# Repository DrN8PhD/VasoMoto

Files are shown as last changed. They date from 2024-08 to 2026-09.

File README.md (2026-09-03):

# VasoMoto
## Monitor and control cannulated vessel pressure in one easy-to-build unit

This arduino-based code is used to program the VasoMoto controller.
Paired with [VasoTracker-2 software](https://github.com/VasoTracker/VasoTracker-2), intravascular pressure can be monitored and controlled without the need for costly interface units.

This system is also capable of simulating pulsatile changes in pressure at rates approaching normal murine heart rate (~400 bpm). A few notes:

* While adaptable to other Arduino versions, this code is specifically written to utilize SAMD51-based microcontrollers. The [ItsyBitsy by Adafruit Inc.](https://www.adafruit.com/product/3800) is recommended.
* A myriad of libraries are required in addition to the custom ones included here.
* The parts list and assembly manual are also included in the release packages.
* This system requires a custom PCB. This is available at a nominal cost through the [Cubi<sup>3</sup>C Core Facility](https://phmtox.msu.edu/facilities/cubi3c) at Michigan State University. Costs will vary depending on the level of assembly you want, but I assure you -- it's far less than any other system on the market.

## v5.0.1
* Bug fixes I missed. 
## v5.0
* This is a complete overhaul of the system's code. Changes for increased stability, better responsiveness and accuracy. Also maintains backward compatibility with original systems.
* Pressure ramps and pulse simulation are functional.
* Pulse simulation gets unpredictable over ~200 bpm. But I call that a win for now.
* Added line filling feature to speed setup of an experiment. It also has a pressure control so you can't destroy your vessel.
* All the menus are now accessible without having to reset the entire box. Calibrations, modes, advanced settings...all can be reached without severing the serial connection to the computer.

## v4.2
* First major update. I noticed that the sampling rate was too high relative to the pressure sensing resolution, resulting in weird pressure oscillations that I couldn't notice until we were tracking pressure with VasoTracker 2. This should all be fixed, resulting in better, more accurate pressure regulation. It's a bit slower for the line filling at first, but this is a small price to pay for healthier vessels.

## v4.1.1
* Added slow pressure ramp. This is different than the step protocol in VasoTracker. This slowly increases the set pressure at a given rate in mmHg/minute.
  
## v4.1.0
* Multiple bug fixes.
* Additional code to allow VasoTracker to control pressure and do timed pressure steps without the need for NI interface.
* Additoonal commenting throughout for clarity in the Arduino code.

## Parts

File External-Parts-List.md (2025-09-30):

# External Parts list
## Here is what you need to purchase to complete this build (USA):

* 3D printed parts included in this GitHub.
* Adafruit [ItsyBitsy M4 Express](https://www.adafruit.com/product/3800). Be sure to get the male and female headers as well! You'll need both to build yourself.
* Stepper motor driver, with equivalent pinout to [this one using the TMC2209 driver](https://www.amazon.com/gp/product/B07ZPV4HFP/).
* [1.8" LCD display module](https://www.amazon.com/gp/product/B07VBSZ2HX).
* [Rotary encoder](https://www.amazon.com/gp/product/B06XQTHDRR/). You will need to modify slightly to change orientation of the pins. So a little soldering is unavoidable until I find an encoder without pins that isn't junk. Note: __this is not a potentiometer__.
* 1.8° stepper motor. Either [NEMA-17](https://www.amazon.com/STEPPERONLINE-Bipolar-Stepper-22-6oz-Extruder/dp/B00PNEQ79Q/) or [NEMA-11](https://www.amazon.com/Iverntech-Stepper-Printer-Machine-Robotics/dp/B07PNV7RBW/) will work with the unit as designed.
* Adjustable AC/DC power supply. I usually use [this one](https://www.amazon.com/gp/product/B07N18XN84/) since it has other tips to use long0-term. __This setup runs at 7.5V__.
* [Silicone tubing](https://www.amazon.com/VictorsHome-Silicone-Flexible-Transfer-Transparent/dp/B09DKWWRSG) with 0.5 mm wall thickness. O.D. does not matter; pump works with 2 mm O.D. – 4 mm O.D. tubing.
* 4-wire pressure transducer. I prefer [these disposable ones from MedLine](https://www.medline.com/product/Head/Z05-PF154670). You can either replace the RJ-11 connector or just cut the robber off to make it more accessible.
* Luer connectors. But if you're reading this, it's my guess you have a box of them in your lab somewhere anyway. (c:
* 3/16" (or 5 mm) set screws. The design used 4-40 thread size since I'm in the USA, but any roughly equivalent diameter will work. 3 are needed for the pump wheel.
* Miscellaneous M3 button cap hex machine screws. Nothing fancy, but the length will depend on which motor you choose.
* [Dry-running MDS-filled nylon sleeve bearing](https://www.mcmaster.com/6294K401/). This is the exact one I used, and you need 3 of them.
* [Acetal dowel pins](https://www.mcmaster.com/97155A426/). These are also the exact ones I use (1/8" diameter, 1/2" long; sorry to metric system colleague). You will need 3 total, but they come in a pack of 50.

### Lastly:
* *PCB with 2-channel custom instrumentation amplifier, integrated stepper motor control and 16-bit ADC ($495 through the MSU Cubi3c Core Facility).*

## Note on the PCB:
So there are probably other ways to do this off-the-shelf, but I designed and built a board for this. I am working on how to make it available through my facilities here at MSU, so please be patient. If you're good at soldering and have a forced-air soldering device, this is doable as a DIY. Otherwise it takes me about 90 minutes to put one together. Futher details on this are available by request.

## Here is what you need to purchase to complete this build (UK):

* 3D printed parts included in this GitHub.
* [Adafruit ItsyBitsy M4 Express (w/ headers)](https://www.digikey.co.uk/en/products/detail/adafruit-industries-llc/3800/9448047).
* [BigTreeTeach TMC2209 V1.3 Stepper motor driver ](https://www.3djake.uk/bigtreetech/stepper-motor-driver?sai=9875).
* [1.8" LCD display module](https://www.amazon.com/gp/product/B07VBSZ2HX).
* [Rotary encoder](https://www.amazon.co.uk/KY-040-Encoder-Development-Arduino-including/dp/B09726Y8RB). 
* 1.8° stepper motor. Either [NEMA-17](https://www.omc-stepperonline.com/nema-17-bipolar-1-8deg-16ncm-22-6oz-in-1a-3-7v-42x42x20mm-4-wires-17hs08-1004s) or [NEMA-11](https://www.amazon.com/Iverntech-Stepper-Printer-Machine-Robotics/dp/B07PNV7RBW/) will work with the unit as designed.
* [Adjustable AC/DC power supply](https://www.amazon.co.uk/Outtag-Universal-Adapter-Speakers-Routers-Black/dp/B0CKYMPDBY/) 
* [Silicone tubing](https://www.amazon.co.uk/VictorsHome-Silicone-Length-Flexible-Transparent/dp/B0CBJWK7XC/) with 0.5 mm wall thickness. O.D. does not matter; pump works with 2 mm O.D. – 4 mm O.D. tubing.
* 4-wire pressure transducer. I prefer [these disposable ones from MedLine](https://www.acevetsupplies.co.uk/products/ibp-transducer-kit-medex-abbott-42585-05). You can either replace the RJ-11 connector or just cut the robber off to make it more accessible.
* Luer connectors. But if you're reading this, it's my guess you have a box of them in your lab somewhere anyway. (c:
* [3x 3/16" (or 5 mm) set screws. 4-40 thread](https://www.accu.co.uk/imperial-cup-point-setgrub-screws/31301-SSU-4-40-3-16-A4)
* [Miscellaneous M3 button cap hex machine screws](https://www.amazon.co.uk/Stainless-Precise-Tapping-Washers-Assortment/dp/B09J2MNSMZ)
* [3x Needle roller bearings](https://www.bearingboys.co.uk/HK-Series-Drawn-Cup-Needle-Bearings/HK0306-Budget-Drawn-Cup-Needle-Bearing-356063-p) (instead of nylon sleeve bearings)
* [Needle Roller Pins](https://www.bearingboys.co.uk/Loose-Needle-Rollers/3mm-x-118mm-Round-End-Loose-Needle-Rollers-Pack-of-100-456051-p) (instead of acetal dowel pins)

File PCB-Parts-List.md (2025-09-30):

# PCB Parts List
### For those looking for a fun way to spend an afternoon!

|  Qty  |  Description  |  Price  |  Total  |
|  ---  |  ---  |  ---  |  ---  |
|  1  |  Custom VasoMoto4 PCB (v1)  |  $40.00  |  $40.00  |
|  1  |  [Adafruit ItsyBitsy M4](https://www.adafruit.com/product/3800)  |  $14.95  |  $14.95  |
|  1  |  [1.8" SPI TFT Display](https://www.amazon.com/1-8inch-LCD-Display-Module-Communicating/dp/B07VBSZ2HX?th=1)  |  $13.43  |  $13.43  |
|  1  |  [NEMA 17 Stepper Motor (short body)](https://www.amazon.com/STEPPERONLINE-Bipolar-Stepper-22-6oz-Extruder/dp/B00PNEQ79Q)  |  $11.99  |  $11.99  |
|  1  |  [TMC2209 Stepper Driver](https://www.amazon.com/BIGTREETECH-TMC2209-Stepper-Printer-Motherboard/dp/B08SMDY3SQ/?th=1)  |  $13.99  |  $13.99  |
|  1  |  [Rotary Encoder](https://www.amazon.com/gp/product/B06XQTHDRR)  |  $9.29  |  $9.29
|  1  |  [DC Power Jack with Switch](https://www.adafruit.com/product/3642)  | $1.95	|	$1.95 |
|  1  |  [AD8426ACPZ Amplifier](https://www.mouser.com/ProductDetail/Analog-Devices/AD8426ACPZ-R7?qs=%2FtpEQrCGXCy0%2F9Zrxy%252BnYw%3D%3D)  | $8.24	|	$8.24 |
|  2  |  [ADA4500 Amplifier](https://www.mouser.com/ProductDetail/Analog-Devices/ADA4500-2ARMZ?qs=BpaRKvA4VqHOSyw3sQK59Q%3D%3D)  | $4.97	|	$9.94 |
|  1  |  [ADS1115 16-bit ADC](https://www.mouser.com/ProductDetail/Texas-Instruments/ADS1115BQDGSRQ1?qs=34RfhUjJmKdvyLrkbnfjHA%)  | $5.83	|	$5.83 |
|  1  |  [L7805CV Linear Voltage Regulator (5 V)](https://www.mouser.com/ProductDetail/STMicroelectronics/L7805CV?qs=9NrABl3fj%2FqplZAHiYUxWg%3D%3D)  | $0.50	|	$0.50 |
|  2  |  [RJ25 Jack](https://www.mouser.com/ProductDetail/571-5555165-1)  | $0.99	|	$1.98 |
|  1  |  [ItsyBitsy Female Headers (Pack)](https://www.adafruit.com/product/4174)  | $1.25	|	$1.25 |
|  2  |  [8-pin Female Header](https://www.mouser.com/ProductDetail/TE-Connectivity/535541-6?qs=ZDXmSm13592BeyHKSexOiA%3D%3D)  | $1.41	|	$2.82 |
|  1  |  [Male Pin Headers (minimum 20 total pins)](https://www.mouser.com/ProductDetail/Molex/22-28-4200?qs=GAPJcf4kvdv8LEkug6BEWQ%3D%3D)  | $0.86	|	$0.86 |
|  6  |  [1x2 Screw Terminal (3.5 mm)](https://www.mouser.com/ProductDetail/Adam-Tech/EBWA-02-A?qs=HoCaDK9Nz5cgBIK%2FOdkl1w%3D%3D)  | $0.49	|	$2.94 |
|  2  |  [10 kOhm Trimmer Resistor](https://www.mouser.com/ProductDetail/652-3314J-1-103E)  | $1.58	|	$3.16 |
|  1  |  [100 µF aluminum polymer capacitor](https://www.mouser.com/ProductDetail/Panasonic/16SEPC100M%2bTSS?qs=OE1iw1LrrPEAt2lEmEitdA%3D%3D)  | $0.89	|	$0.89 |
|  1  |  [10 µF capacitor (US1206)](https://www.mouser.com/ProductDetail/YAGEO/CC1206ZKY5V7BB106?qs=rEZiXmXGZa%2FuXF99zRq3Vg%3D%3D)  | $0.24	|	$0.24 |
|  1  |  [0.33 µF ceramic capacitor](https://www.mouser.com/ProductDetail/KEMET/C324C334M5U5TA?qs=sGAEpiMZZMsh%252B1woXyUXj%2FPRwpp8kXWD%2F6VAC8Qms%2F0%3D)  | $0.49	|	$0.49 |
|  1  |  [0.1 µF capacitor (US1206)](https://www.mouser.com/ProductDetail/KEMET/C1206C104K5RACTU?qs=VbFpUC1cecnmBMAUeCQCPw%3D%3D)  | $0.10	|	$0.10 |
|  2  |  [0.015 µF (15 nF) capacitor (US1206)](https://www.mouser.com/ProductDetail/KEMET/C1206C153K5RACTU?qs=kei6kuvHAl88e3ElWIo0oA%3D%3D)  | $0.21	|	$0.42 |
|  7  |  [0.01 µF (10 nF) capacitor (US1206)](https://www.mouser.com/ProductDetail/KEMET/C1206C103M5RACTU?qs=C9xViIFka8k6tXd6%2Fqf7IA%3D%3D)  | $0.11	|	$0.77 |
|  2  |  [14.3 kOhm Resistor (US1206)](https://www.mouser.com/ProductDetail/YAGEO/RC1206FR-0714K3L?qs=ncxkyCpAYDBq1S9aCtJYCQ%3D%3D)  | $0.10	|	$0.20 |
|  3  |  [10 kOhm Resistor (US1206)](https://www.mouser.com/ProductDetail/YAGEO/RC1206FR-0710KL?qs=%252BhB4WxZmbVEJV82xdVgRUw%3D%3D)  | $0.10	|	$0.30 |
|  2  |  [7.32 kOhm Resistor (US1206)](https://www.mouser.com/ProductDetail/YAGEO/RC1206FR-077K32L?qs=afJZr%2F7kGG6v1eT3E1VQ7A%3D%3D)  | $0.10	|	$0.20 |
|  2  |  [91 Ohm Resistor (US1206)](https://www.mouser.com/ProductDetail/YAGEO/RC1206JR-0791RL?qs=2fXw4cjoqb%2FCE9bK5gFcaQ%3D%3D)  | $0.10	|	$0.20 |
|  1  |  [3V – 12VDC power supply](https://www.amazon.com/gp/product/B07N18XN84)  | $15.90	|	$15.90 |
|  1  |  [Crimping Tool Kit](https://www.amazon.com/gp/product/B07R1H3Z8X)  | $34.99	|	$34.99 |
|  ---  |  ---  |  ---  |  ---  |
|    |    |  **Total:**  |  **$197.82**  |

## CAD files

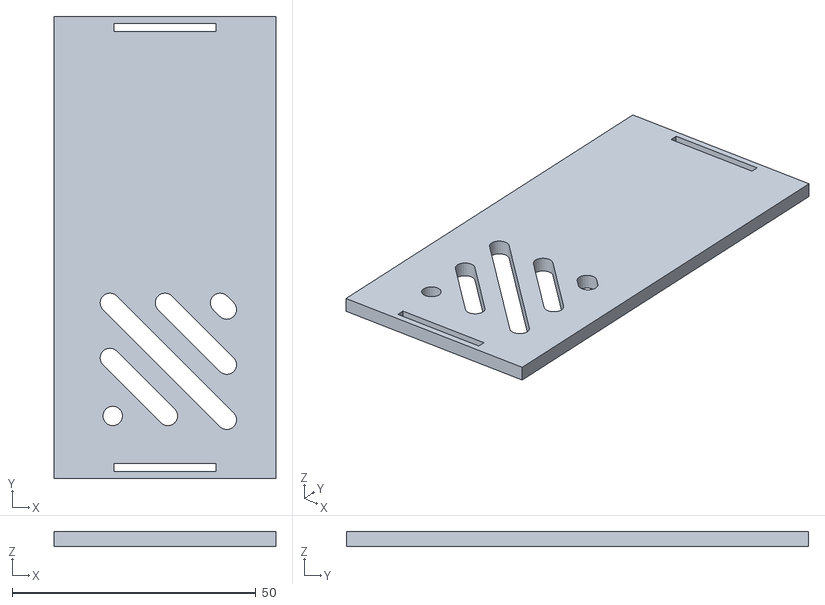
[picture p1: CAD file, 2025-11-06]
VasoMoto Printed Parts/VasoMoto-front.stl
45.5 x 94.8 x 3.00

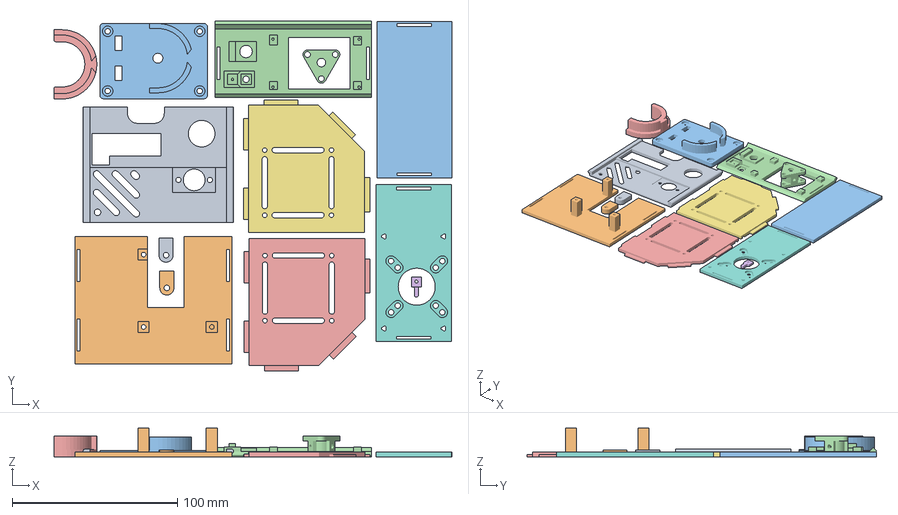
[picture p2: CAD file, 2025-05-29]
VasoMoto Printed Parts/VasoMoto_Core_One_All.3mf
240.8 x 211.5 x 17.5 mm
VasoMoto-back.stl
VasoMoto-base.stl
VasoMoto-front.stl
VasoMoto-LCD-button.stl
VasoMoto-left-side.stl
VasoMoto-optional-clip.stl
VasoMoto-right-side.stl
VasoMoto-Top.stl
VasoMoto-tube-holder.stl x 2
VasoMoto-pump.stl
VasoMoto-pumphead.stl
VasoMoto-tubing-spacer-2.stl

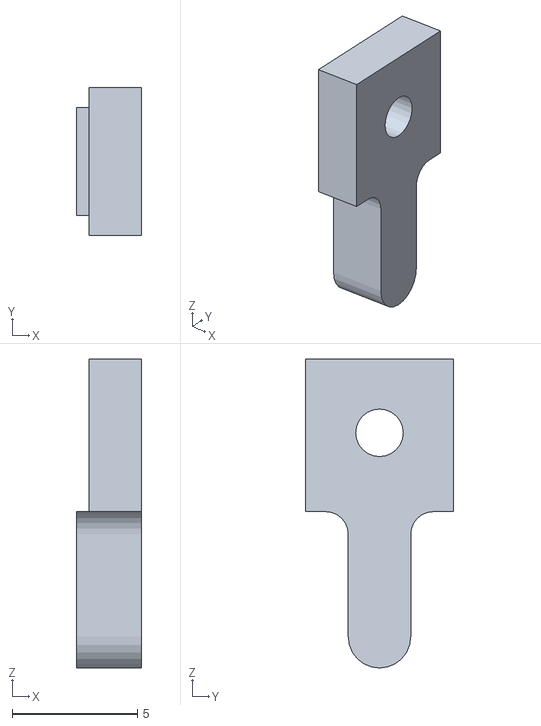
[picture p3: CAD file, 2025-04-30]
VasoMoto Printed Parts/VasoMoto-optional-clip.stl
2.60 x 5.90 x 12.3

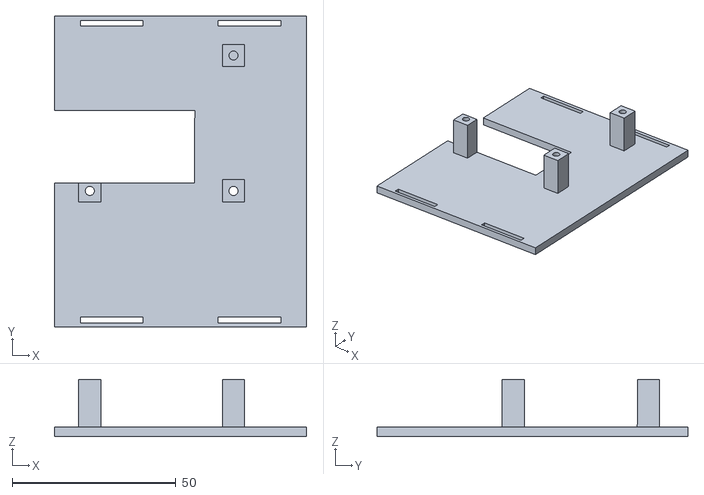
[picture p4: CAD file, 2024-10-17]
VasoMoto Printed Parts/VasoMoto-base.stl
76.9 x 94.8 x 17.5

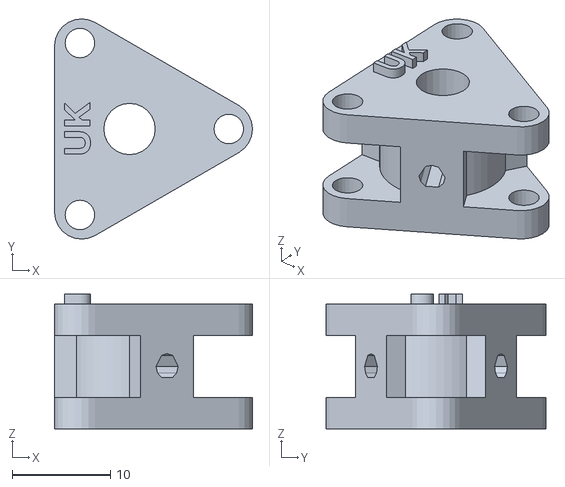
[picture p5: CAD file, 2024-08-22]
VasoMoto Printed Parts/VasoMoto-pumphead-UK.stl
20.1 x 22.4 x 13.7

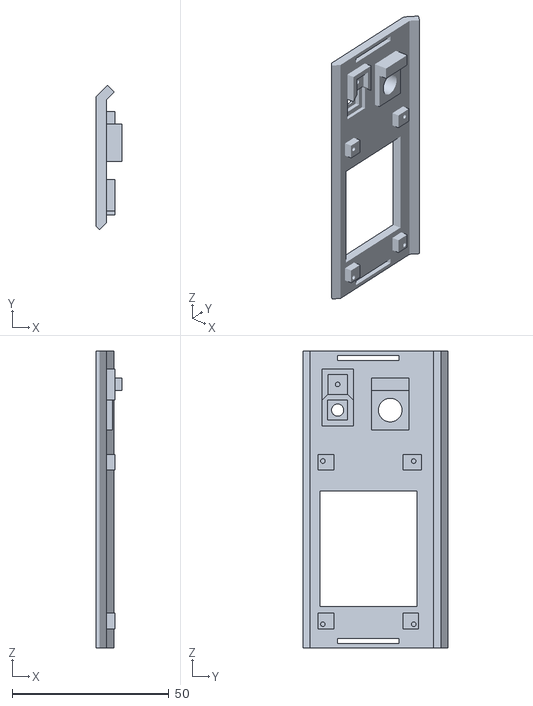
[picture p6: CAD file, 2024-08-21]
VasoMoto Printed Parts/VasoMoto-LCD-button.stl
8.29 x 46.2 x 94.8

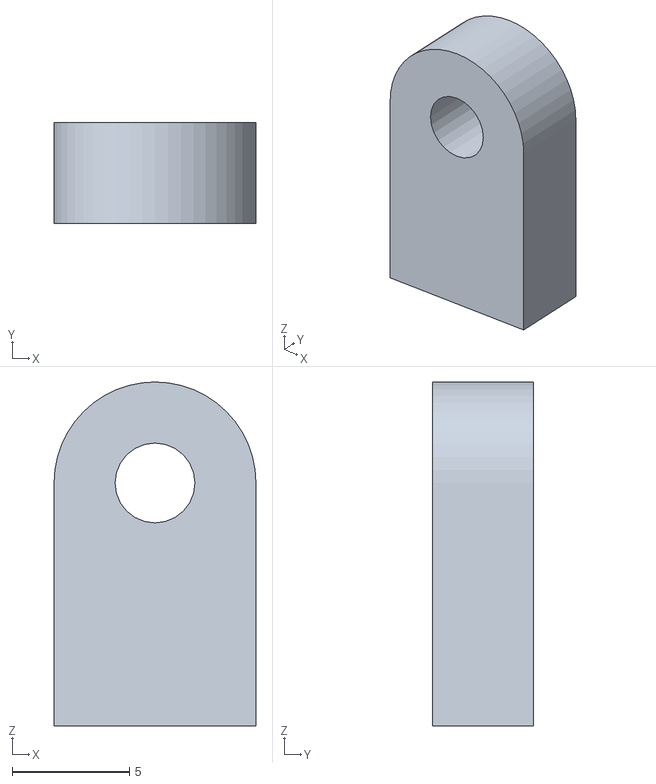
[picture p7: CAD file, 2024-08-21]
VasoMoto Printed Parts/VasoMoto-tube-holder.stl
8.60 x 4.30 x 14.7

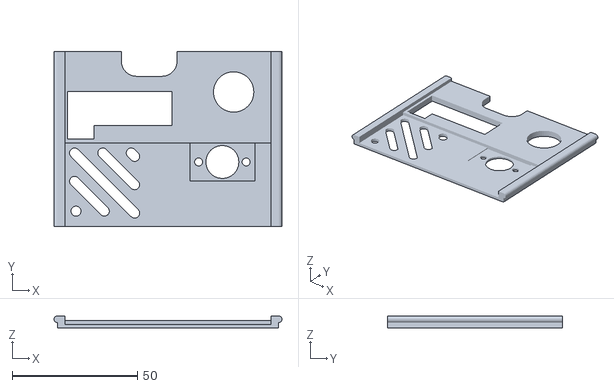
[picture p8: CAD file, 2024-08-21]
VasoMoto Printed Parts/VasoMoto-back.stl
91.0 x 70.0 x 4.80

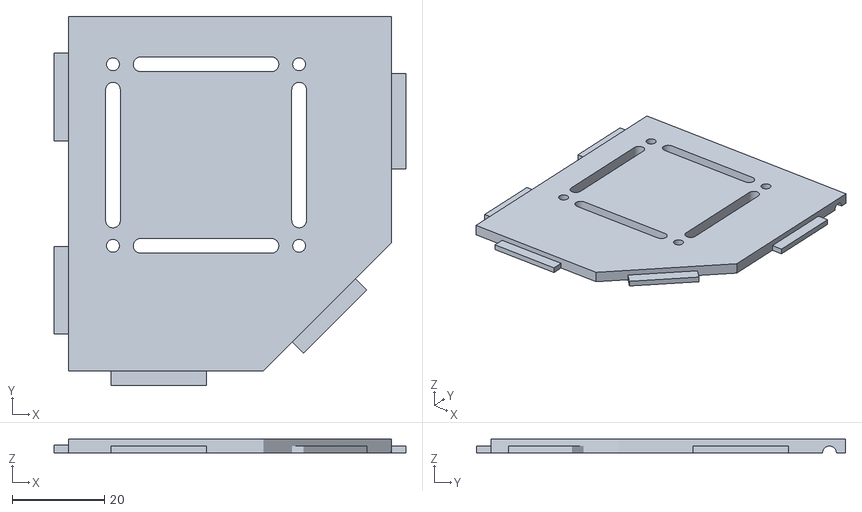
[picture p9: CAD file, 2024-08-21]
VasoMoto Printed Parts/VasoMoto-left-side.stl
76.4 x 80.1 x 3.03

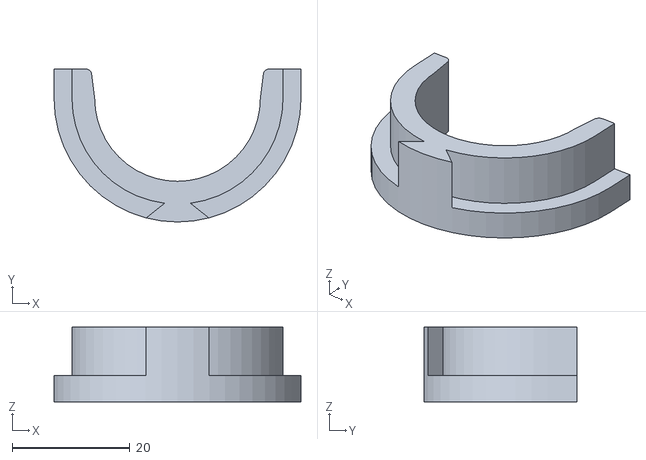
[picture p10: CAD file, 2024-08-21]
VasoMoto Printed Parts/VasoMoto-tubing-spacer-1.stl
41.9 x 26.0 x 12.7

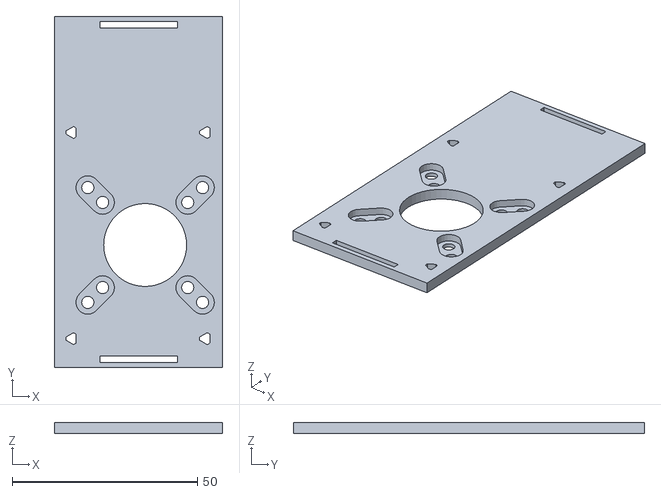
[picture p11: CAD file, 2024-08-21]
VasoMoto Printed Parts/VasoMoto-Top.stl
45.5 x 94.8 x 3.00

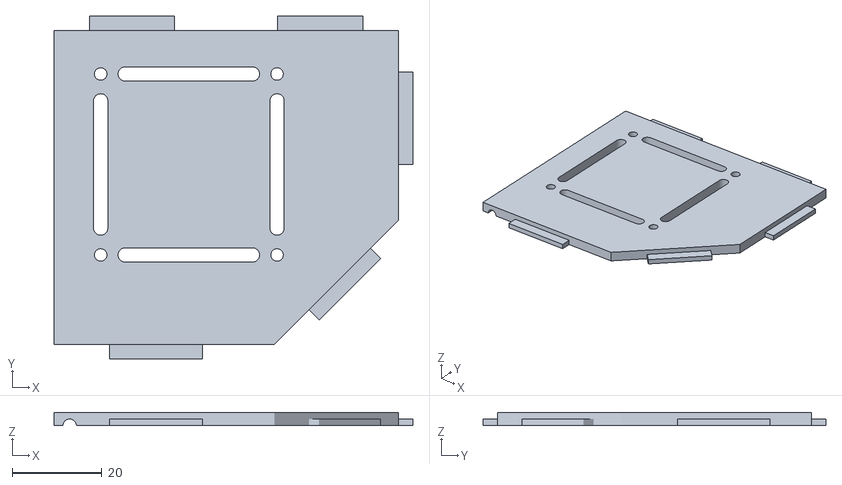
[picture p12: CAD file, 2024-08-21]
VasoMoto Printed Parts/VasoMoto-right-side.stl
80.1 x 76.5 x 3.00

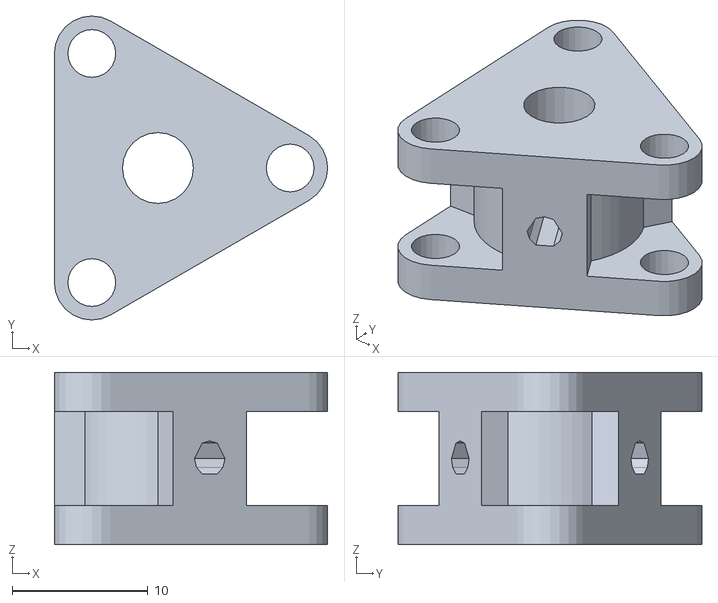
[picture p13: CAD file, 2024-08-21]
VasoMoto Printed Parts/VasoMoto-pumphead.stl
20.1 x 22.4 x 12.7

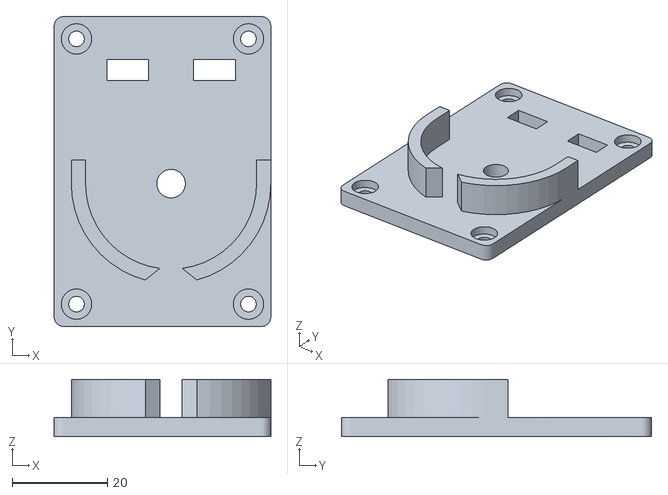
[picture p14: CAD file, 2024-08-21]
VasoMoto Printed Parts/VasoMoto-pump.stl
45.5 x 65.1 x 12.0

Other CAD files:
VasoMoto Printed Parts/VasoMoto-LCD-no-button.stl
VasoMoto Printed Parts/VasoMoto-tubing-spacer-2.stl

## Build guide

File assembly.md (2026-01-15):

# Assembly Instructions
## Prior to Beginning:
1) Acquire all parts listed in the "external-parts-list.md" file.
2) Print all required parts in the "VasoMoto Printed Parts" folder. Note that UK and US have different pump heads to print. This is due to differences in parts availability. The UK parts are prototyped, but not tested in practice yet.
3) Every rotary encoder I can find has bent pins that are on the wrong side. You will need to de-solder the 5 bent pins and solder 5 straight pins in their place. Make sure the ones you're replacing are on the **opposite side of the circuit board from the knob.** See below for a clearer picture.
4) This guide assumes you have fabricated or purchased the completed PCB that makes up the "heart" of the VasoMoto controller. A separate manual in the works for how to fabricate the VasoMoto controller from scratch with the "blank" PCB.

##  **Step 1: Lay out all the pieces.**
Everything is shown here, except the pump head and fasteners. They'll be pictured later. The pieces are as follows:
1)  Front plate
2)  Stepper motor NEMA 17 stepper motor
3)  Pump plate
4)  VasoMoto controller PCB
5)  LCD plate
6)  1.8" LCD module
7)  Back plate
8)  Arduino
9)  Rotary encoder and stepper motor driver
10) Motor plate
11) Left side plate
12) Right side plate
13) Base plate
VasoMoto parts laid out

##  **Step 2: Get the fasteners together.**
Fasteners needed are shown below. Where there is flexibility in sizing, I've made that note. We will be assembling efverything __but__ the pump head right now.

1)  1/4" No. 2 sheet metal screws (4). These need to be the 'pointy' kind of screw. They attach the LCD diplay to the LCD plate.
2)  M3 x 4 mm button cap screws (4). These are the 'flat' kind of screws. They attach the motor to the motor plate
3)  M3 x 6 mm button cap screws (4). THey can be longer than 6 mm but not shorter. They attach the pump to the motor plate.
4)  The screws off of the LCD display stand-offs (3). If you got an LCD without these screws, just use 3 more M3x6 screws instead.

assembly screws

##  **Step 3: Assemble VasoMoto controller.**
Insert the arduino in the bottom of the PCB in the appropriate headers. Insert the stepper motor driver in the proper headers on the top. Note that the proper "DIR" and "GND" pins on the header are in the spots marked "DIR" and "GND" on the PCB.

Assembled PCB

##  **Step 4: Attach the VasoMoto controller top the base plate.**
Use 3 screws. THe holes aren't threaded, so it might be easier to screw them in without the controller first to cut some threads in the plastic. You might have to pop the stepper driver back out, depending on what size screw and screwdriver you have.

PCB affixed to baseplate

##  **Step 5: Assemble the LCD plate.**
1) If opresent, remove all 4 brass standoffs from the display. no need to connect any cables just yet. Not the direction of the connector -- the LCD only fits in the plate one way. LCD in LCD plate
2) Using 4 No. 2 machine screws, attach the LCD module to the LCD plate. Do NOT overtighten, or the screws will poke through the front of the plate.
3) Insert the rotary econder with the pins placed as noted in the photo. Ignore that extra wire and button -- that's not needed for this build. Attach the rotary encoder using the nut and washer that comes with it.

LCD and rotary encoder in place

##  **Step 6: Prepare and connect the rotary encoder wiring harness.**
These next two parts Are probably the trickier bits since there are a bunch of different ways to do it. I have a crimper and connectors, so I make my own wires. But this can be done with [10 cm female-to-female jumper wires](https://www.amazon.com/dp/B07S2RH6Q4/).
 1)  Connect the roatry encoder to the VasoMoto controller using 5 jumper wires. This is the easy part. Each pin's identity is printed on the front, so the image below tells you what each one is. 

rotary encoder pinout
PCB pinout for encoder

2)  Once connected, it should look like the image below. As you can see I have 5-pin DIN headers and shorter wires, but there is plenty of space in the VasoMoto enclosure to cram the excess 10 cm retail jumper wires.

connected encoder

##  **Step 7: Prepare and connect the LCD wiring harness.
Now for the trickier part. If you can, get some [8-pin female dupont connector housings](https://www.amazon.com/2-54mm-Dupont-Connector-Housing-Female/dp/B0BG7CZ2F9/). This makes connecting and disconnecting a LOT easier....but you can also use the connectors on the LCD harness if you want to save a few bucks. The reaason the order is different on the board compared to the module is...complicated. But it has to be this way.

As you can see, there are 8 wires, labaled and color coded as below:

LCD wires with labels

The problem is the order they go onto the VasoMoto controller is **DIFFERENT THAN THE ORDER THEY ARE ON THE LCD!**

board pinout LCD

So...we either need to make a new 8-pin connector or connect each wire individually to the VasoMoto controller.

**Option 1: Making a new Connector**
1)  Using a small screwdriver, pop the plastic tab on the Dupont connectors on each individual wire. This image, from left to right, shows the intact connector, a connector with the tab bent up, and a wire with the connector removed. They should just slide right off without much force.removing dupont connector

2)  Clip all 8 wires into the new 8-pin dupont connector, making sure they are in the proper order. It's the name on the wire that's important, not the color...so if your colors are different than mine, adjust to make the pinout correct.

8-pin connector

**Option 2: Connect each wire to the board individually.**
This is self-explanatory, but I'll tell you why it's harder. If you need to remove the display, you have to disconnect all 8 wires...and then you have to remember the order that they go in, which is not the same as the order on the LCD module. I make these all the time, and I can't remember what goes to what (other than the white wire is ground). So...spend a few bucks and make the 8-pin connector -- or take lots of photos of the wiring order.

##  **Step 8: Mount the motor to the pump.
1)  Using 4, M3x4 screws, attach the NEMA17 stepper motor to the motor plate. There are 2 sets of motor plate holes, in case someone uses a NEMA 11 instead. Either way, it's stil the same size screws. Make sure the motor is oriented so that the wires point the direction shown below:

motor wire direction

2)  Using 4, M3x6 (or longer) screws, attach the pump to the motor plate. In the photo, the tubing spacer is already in place. THat can stay out for now. No need to connect wires -- we will do that later.

mounted motor

##  **Step 9: Assemble the rest of the VasoMoto controller box.
1) Start with the back, then the sides. Notice the groove on each side plate; it should face inward toward the back plate. The sides shopuld press tightly into the slots on the base plate.

sides and back in place

4) Connect the motor wires, in the order shown below, to the screw terminals on the VasoMoto controller. Sometimes the terminals are all screwed the way down, so make sure and loosen the screws first. If you wire colors are different, the proper assignments for each wire are printed on the PCB (e.g., A+, A-, B+, B-). Leave the motor plate off to the side for now.

motor wiring

5)  Connect the LCD module and rotary encoder to the VasoMoto control board, but do not place the LCD on the controller box yet.

LCD plate connected

6)  Put the motor plate in place.

motor in place

6)  Now you can put the LCD plate in place. Finish it off by cramming the wires inside and putting the front plate on it! Now all that's left is the pump head.

completed box without pump head

##  **Step 10: Assemble and attach the pump head.
1) Gather all the parts. This includes the printed pump head, 3 bushings, 3 acetyl rods, and 3 3/16" set screws. Note: when printing the print head, it's best to print in the orientation shown below (using supports where needed). It is important that the pump head is as circular as possible for proper pump function.

pump head parts

3) Screw the set screws in place around the pump head. NO need to insert fully -- just 1-2 turns is sufficient for now.

set screws in place

4) Insert rods and bushings. These are just press-fit into place. Do NOT glue the rods in place! Make sure the bushings turn freely. If not, remove the rods, sand the inside surfaces of the print head arms, and re-assemble.

completed pump head

5)  Place the pump head on the motor shaft. Align one set screw with the notch on the motor shaft and screw in place. Turn the pump head and repeat for the other two screws.

tightening pump head

7)  Place the tubing spacer. You need not glue it in place, but you might find you want to after testing the pump later. Insert tubing through the tubing holders and around the pump head. You don't want it too short that it has to stretch over the pump head; nor do you want it too long that it bunches up on either side. You want it just taught enough to stay in place.

tubing in place

##  **Step 11: POWER ON!  You're done!

completed unit

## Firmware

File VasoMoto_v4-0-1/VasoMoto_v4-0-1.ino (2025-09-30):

/* This version includes external input to change pressure. All tension recording functions are disabled. Can be re-enabled for a second pressure
   transducer, but name should be changed to prevent confusion. */

#include <Wire.h>
#include "bitmaps.h"
#include "FlashStorage.h"
#include "avr/dtostrf.h"
#include <SPI.h>
#include <Adafruit_GFX.h>
#include "FreeSansBold7pt7b.h"
#include "FreeSansBold8pt7b.h"
#include "FreeSansBold9pt7b.h"
#include <Adafruit_ST7735.h>  // Hardware-specific library
#include "stepper.h"

/*ADC Setup*/
  ADS1115 ads;
  byte calibrationOrder;

/*TFT Setup*/
  #define TFT_CS A4
  #define TFT_DC A3
  #define TFT_RST 13  // Or set to -1 and connect to Arduino RESET pin. This only needs to be 13 when using TensoMoto board v2.0 (May 2023)
  Adafruit_ST7735 tft = Adafruit_ST7735(TFT_CS, TFT_DC, TFT_RST);
  int rainbow[34]{ 0x001F, 0x011F, 0x021F, 0x031F, 0x041F, 0x051F, 0x061F, 0x071F, 0x07FF, 0x07FC, 0x07F8, 0x07F4, 0x07F0, 0x07EC, 0x07E8, 0x07E4, 0x07E0, 0x27E0, 0x47E0, 0x67E0, 0x87E0, 0xA7E0, 0xC7E0, 0xE7E0, 0xFFE0, 0xFF00, 0xFE00, 0xFD00, 0xFC00, 0xFB00, 0xFA00, 0xF900, 0xF800 };

/*Rotary Encoder Setup and interrups*/
  #define pinDC 10
  #define pinCS 11
  #define enSW 12 
  volatile byte aFlag = 0;        //  let's us know when we're expecting a rising edge on pinDT to signal that the encoder has arrived at a detent
  volatile byte bFlag = 0;        //  let's us know when we're expecting a rising edge on pinCLK to signal that the encoder has arrived at a detent (opposite direction to when aFlag is set)
  int encoderPos;                 //  this variable stores our current value of encoder position. Change to int or uin16_t instead of byte if you want to record a larger range than 0-255
  volatile uint32_t reading = 0;  //  somewhere to store the direct values we read from our interrupt pins before checking to see if we have moved a whole detent
  uint32_t maskA;
  uint32_t maskB;
  uint32_t maskAB;
  volatile uint32_t *port;
  bool box;
  int runStateSim = 0;
  int runStateMoto = 0;
  bool fillLines = false;
  bool printSettings = true;
  int choice;
  bool beatDir;

  void fpinDC() {
    noInterrupts();
    reading = *port & maskAB;
    if ((reading == maskAB) && aFlag) {  //check that we have both pins at detent (HIGH) and that we are expecting detent on this pin's rising edge
      encoderPos--;                      //decrement the encoder's position count
      box = !box;
      bFlag = 0;  //reset flags for the next turn
      aFlag = 0;  //reset flags for the next turn
    } else if (reading == maskB) bFlag = 1;
    interrupts();  //signal that we're expecting pinCS to signal the transition to detent from free rotation
  }
  void fpinCS() {
    noInterrupts();
    reading = *port & maskAB;
    if (reading == maskAB && bFlag) {  //check that we have both pins at detent (HIGH) and that we are expecting detent on this pin's rising edge
      encoderPos++;                    //increment the encoder's position count
      box = !box;
      bFlag = 0;  //reset flags for the next turn
      aFlag = 0;  //reset flags for the next turn
    } else if (reading == maskA) aFlag = 1;
    interrupts();  //signal that we're expecting pinDC to signal the transition to detent from free rotation
  }

/*Stepper Setup*/
  Stepper stepper(0, 9, 7, 5, 2, 3);
  unsigned long currentMicros;
  unsigned long previousMicros = 0;
  int pulseCounter = 0;
  float tempRate = 0.0;
  float actualRate = 0.0;
  int maxDelay = 30000;   //  Used in pressureControl to easily alter how slow the stepper starts, so I dont have to change in 12 places.
  int numSteps = 0;
  int stepCounter = 0;
  int stepsPerSec = 200;  //This is WHOLE steps per sec; the fractionation is accounted for later.
  int goUp = maxDelay;
  int goDown = maxDelay;
  int x = 1;
  int y = 1;

/*Pressure sensor calibration and setup*/
  int txdx1 = 0;                      //identity of first transducer
  int txdx2 = 1;                      //identity of second transducer
  int iMinP = 0;           // Raw value calibration lower point
  int iMaxP = 65535;       // Raw value calibration upper point
  float avgPressure = 0.0;
  float avgTension = 0.0;
  float avgSample = 0.0;
  float oMinP = 0.0;      // Pressure calibration lower point
  float oMaxP = 200.0;    // Pressure calibration upper point. This is in mmHg. This is about the max it can do.
  float PRESSURE_CAL_MIN = 0.00;
  float PRESSURE_CAL_MAX = 80.0;
  int iMinT = 0;            // Raw value calibration lower point
  int iMaxT = 65535;        // Raw value calibration upper point
  float oMinT = 0.0;       // Pressure calibration lower point
  float oMaxT = 1000.0;    // Pressure calibration upper point. This is in µN. This is about the max it can do.
  float TENSION_CAL_MIN = 0.00;
  float TENSION_CAL_MAX = 100.0;

/*Flash storage definitions and matrices*/
   struct cal_matrix {       //place to store all the values needed for linear calibration of sensors.
    bool valid;
    float _pLowSel;
    float _pHiSel;
    float _tLowSel;
    float _tHiSel;
    int _pLowADC;
    int _pHiADC;
    int _tLowADC;
    int _tHiADC;
  } calib;

    float pLowSel;
    float pHiSel;
    float tLowSel;
    float tHiSel;
    int pLowADC;
    int pHiADC;
    int tLowADC;
    int tHiADC;
 
   struct init_matrix {    //place to store all the values from the "advanced" settings menu.
    bool valid;
    int _timeDelay;         //the time delay for wheatstone bridge output.
    int _filterWeight;      //the weighting of the averaging filter.
    float _multiplier;      //Use this to set the velocity multiplier to get the right shape of the pressure curve.             
    int _acceleration;      //Use this to alter how fast the pump accelerates and to what speed.
    int _numSamples;        //the number of samples averaged. Was set to 5 in v200 for some reason?
  } startup;

  int timeDelay;       
  int filterWeight;    
  float multiplier;    
  int acceleration;    
  int numSamples;      
 
   struct sim_matrix {     //place to store values of the pulse simulation.
    bool valid;
    int _minmmHg;
    int _maxmmHg;
    int _pulseRate;
  } sim;

    int minmmHg;
    int maxmmHg;
    int pulseRate;
  
  FlashStorage(calibrate, cal_matrix);
  FlashStorage (initialize, init_matrix);
  FlashStorage(simulation, sim_matrix);

/*Serial receive vairables*/
  const byte numChars = 16;
  char receivedChars[numChars];
  bool newData = false;

/*Miscellaneous global variables*/
  unsigned long previousMillis = 0;
  unsigned long prevmillis = 0;
  unsigned long currmillis;
  unsigned long startMillis;
  unsigned long currentMillis;
  unsigned long newTime;
  double currentTime;
  int expType;
  int initMin = 60;     //Change this to alter min pressure starting point
  int initMax = 100;    //Change this to alter max pressure starting point
  int initSteps = 60;  //Change this to alter the pulse rate starting point
  int beatTime;
  int pulseInt;
  int ticker;
  float coloring;
  int sel_pressure = 0;
  bool UseStartTime = true;
  bool moto = false;
  char number[8];
  char selected[4];
  char pressure[6];
  char tension[6];
  char range[8];
  char rate[6];
  char time[12];
  char RunningOutputMoto[28];
  char StoppingOutputMoto[28];
  char RunningOutputSim[32];
  char StoppingOutputSim[32];
  char pressureBufferLCA[32];  //Pressure calib.pLowADC string
  char pressureBufferHCA[32];  //Pressurecalib.pHiADC string
  char pressureBufferLCS[32];  //Pressure calib.pLowSel string
  char pressureBufferHCS[32];  //Pressure calib.pHiSel string
  char tensionBufferLCA[6];  //Tension low_cal_ADC string
  char tensionBufferHCA[6];  //Tension high_cal_ADC string
  char tensionBufferLCS[4];  //Tension low_cal_sel string
  char tensionBufferHCS[4];  //Tension high_cal_sel string
  char bufferLP[32];   //low pressure string
  char bufferHP[32];   //high pressure string
  char bufferPR[32];   //pulse rate string
  char debugging[50]; //for ease of reading serial output stuff

void setup() {
  Serial.begin(115200);
  ads.begin();
  ads.setGain(GAIN_ONE);
  pinMode(enSW, INPUT_PULLUP);
  pinMode(pinCS, INPUT_PULLUP);
  pinMode(pinDC, INPUT_PULLUP);
  attachInterrupt(pinDC, fpinDC, CHANGE);  //Sets interrupt for rotary encoder so that it works with above functions;
  attachInterrupt(pinCS, fpinCS, CHANGE);
  maskA = digitalPinToBitMask(pinDC);
  maskB = digitalPinToBitMask(pinCS);
  maskAB = maskA | maskB;
  port = portInputRegister(digitalPinToPort(pinDC));
  stepper.begin();
  tft.initR(INITR_GREENTAB);
  tft.initR(INITR_BLACKTAB);
  tft.fillScreen(ST7735_BLACK);
  tft.setRotation(1);
  tft.setTextWrap(false);
  
  startup = initialize.read();
  calib = calibrate.read();
  sim = simulation.read();

  loadingFromFlash();

  bootup();
  chooseMode();
  calibration();
  ads.linearCal(pLowADC, pHiADC, pLowSel, pHiSel);
  // ads.linearCal(tLowADC, tHiADC, tLowSel, tHiSel);
  if(moto == true) {
    stepper.setStepFrac(8);
    clickBegin();
    delay(500);
  }
  if(moto == false) {
    stepper.setStepFrac(8);
    stepper.setStepFracSpeed(8, stepsPerSec);
    bootSim();
    testType();
  }
while (fillLines == true) {
      lineFilling();
      tft.fillScreen(ST7735_BLACK);
      initScreenSim();
      printWords(9, 1, 102, 39, 0xfb2c, "Done");
      printNumber(2, 110, 47, 0xfb2c, ST77XX_BLACK, minmmHg);
      printNumber(2, 110, 67, 0xfb2c, ST77XX_BLACK, maxmmHg);
      printNumber(2, 110, 87, 0xfb2c, ST77XX_BLACK, pulseRate);
      testType();
      // delay(500);
    }
stepper.setStepFracSpeed(8, stepsPerSec);
writingToFlash();
initialize.write(startup);
}

void loop() {
  currentMillis = millis();
  if(moto == false) {
    if (runStateSim == 0) {
      isStoppingSim();
    } else if (runStateSim == 1) {
      isRunningSim();
    }
  }
  else if(moto == true) {
    if (runStateMoto == 0) {
      isStoppingMoto();
    } else if (runStateMoto == 1) {
      isRunningMoto();
    }
  }
}
//************************************************************************************************************************//

void loadingFromFlash() {
  timeDelay = startup._timeDelay;
  filterWeight = startup._filterWeight;
  multiplier = startup._multiplier;
  acceleration = startup._acceleration;
  numSamples = startup._numSamples;
  pLowSel = calib._pLowSel;
  pHiSel = calib._pHiSel;
  tLowSel = calib._tLowSel;
  tHiSel = calib._tHiSel;
  pLowADC = calib._pLowADC;
  pHiADC = calib._pHiADC;
  tLowADC = calib._tLowADC;
  tHiADC = calib._tHiADC;
  minmmHg = sim._minmmHg;
  maxmmHg = sim._maxmmHg;
  pulseRate = sim._pulseRate;
}

void writingToFlash() {
  startup._timeDelay = timeDelay;
  startup._filterWeight = filterWeight;
  startup._multiplier = multiplier;
  startup._acceleration = acceleration;
  startup._numSamples = numSamples;
  calib._pLowSel = pLowSel;
  calib._pHiSel = pHiSel;
  calib._tLowSel = tLowSel;
  calib._tHiSel = tHiSel;
  calib._pLowADC = pLowADC;
  calib._pHiADC = pHiADC;
  calib._tLowADC = tLowADC;
  calib._tHiADC = tHiADC;
  sim._minmmHg = minmmHg;
  sim._maxmmHg = maxmmHg;
  sim._pulseRate = pulseRate;
}

void recvWithStartEndMarkers() {
  static bool recvInProgress = false;
  static byte ndx = 0;
  char startMarker = '<';
  char endMarker = '>';
  char rc;
  while (Serial.available() > 0 && newData == false) {
    rc = Serial.read();
    if (recvInProgress == true) {
      if (rc != endMarker) {
        receivedChars[ndx] = rc;
        ndx++;
        if (ndx >= numChars) {
          ndx = numChars - 1;
        }
      }
      else {
        receivedChars[ndx] = '\0'; // terminate the string
        recvInProgress = false;
        ndx = 0;
        newData = true;
      }
    }
    else if (rc == startMarker) {
      recvInProgress = true;
    }
  }
}

void showNewData() {
  if (newData == true) {
    encoderPos = atoi(receivedChars);
    newData = false;
  }
}
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

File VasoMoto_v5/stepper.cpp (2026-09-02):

#include "stepper.h"
#include <Arduino.h>
#include <Wire.h>
//constructor
Stepper::Stepper(int stepPin, int dirPin, int enPin, int vHiPin, int m0Pin, int m1Pin)
{
  _stepPin = stepPin;
  _dirPin = dirPin;
  _enPin = enPin;
  _vHiPin = vHiPin;
  _m0Pin = m0Pin;
  _m1Pin = m1Pin;

  _previous_us = 0;
  _current_us = 0;
}

void Stepper::begin()
{
  pinMode(_stepPin, OUTPUT);
  pinMode(_dirPin, OUTPUT);
  pinMode(_enPin, OUTPUT);
  pinMode(_m0Pin, OUTPUT);
  pinMode(_m1Pin, OUTPUT);
  pinMode(_vHiPin, OUTPUT);
  digitalWrite(_stepPin, LOW);
  digitalWrite(_dirPin, LOW);  //LOW is CW. HIGH is CCW.
  digitalWrite(_enPin, HIGH);
  digitalWrite(_vHiPin, HIGH);
}

void Stepper::disable() {
  if (_isEnabled) {
    digitalWrite(_enPin, HIGH); // Disable motor output
    _isEnabled = false;
  }
}

void Stepper::move(int enable, int stepDelay, int dir) 
{
  // 1. Handle enabling/disabling the motor
  if (enable == 0) {
    disable();
    return;
  }
  
  if (!_isEnabled) {
    digitalWrite(_enPin, LOW); // Active-low enable
    _isEnabled = true;
  }

  // 2. Set the direction (Map the 1 or -1 from the INO to HIGH/LOW)
  int dirState = (dir == 1) ? HIGH : LOW; 
  if (dirState != _currentDir) {
    digitalWrite(_dirPin, dirState);
    _currentDir = dirState;
  }

  // 3. Generate a non-blocking step pulse
  _current_us = micros();
  if (_current_us - _previous_us >= stepDelay) {
    digitalWrite(_stepPin, HIGH);
    delayMicroseconds(2); // A tiny 2-microsecond HIGH pulse is enough for most drivers
    digitalWrite(_stepPin, LOW);
    
    _previous_us = _current_us;
  }
}

void Stepper::setStepFrac(int fraction)
{
  _fraction = fraction;
  //m0-m1:  LOW-LOW is 1/8; LOW-HI is 1/32; HI-LOW is 1/64; HI-HI is 1/16. speed is in rotations per second.
  switch (_fraction) {
    case 8:
      digitalWrite(_m0Pin, LOW);
      digitalWrite(_m1Pin, LOW);
      break;
    case 16:
      digitalWrite(_m0Pin, HIGH);
      digitalWrite(_m1Pin, HIGH);
      break;
    case 32:
      digitalWrite(_m0Pin, LOW);
      digitalWrite(_m1Pin, HIGH);
      break;
    case 64:
      digitalWrite(_m0Pin, HIGH);
      digitalWrite(_m1Pin, LOW);
      break;
  }
}
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

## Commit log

2024-08-21 STL files
    Use the "LCD-no-buttons" if the rotary encoder button works for you. Otherwise, use the "LCD-button" but you'll have to get a button and modify the encoder slightly. "Clip" is only needed if "LCD-but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
    [VasoMoto-LCD-button.stl, VasoMoto-LCD-no-button.stl, VasoMoto-Top.stl, VasoMoto-back.stl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]
2024-08-21 Added power supply
2024-08-21 Added bushings for pump
2024-08-22 Pumphead for UK parts
    [VasoMoto-pumphead-UK.stl]
2024-08-22 Revert "Pumphead for UK parts"
    This reverts commit de97881e48c736914ef631b7fbfe33e05320747d.
    [VasoMoto-pumphead-UK.stl]
2024-08-22 Added pumphead for UK bearings
    [VasoMoto-pumphead-UK.stl]
2024-10-17 General Updates
    [VasoMoto-base.stl]
2025-04-30 New Version
    Updated controls and code
    [VasoMoto-optional-clip.stl]
2025-05-29 Layout for Prusa Core One printer
    [VasoMoto_Core_One_All.3mf]
2025-05-29 Create PCB-Parts-List.md
    For DIY assembly of VasoMoto4 Electronics
2025-11-06 Updated
    For new Release
    [VasoMoto-front.stl]
2025-11-10 Update
    fixed calibration error plaguing me
